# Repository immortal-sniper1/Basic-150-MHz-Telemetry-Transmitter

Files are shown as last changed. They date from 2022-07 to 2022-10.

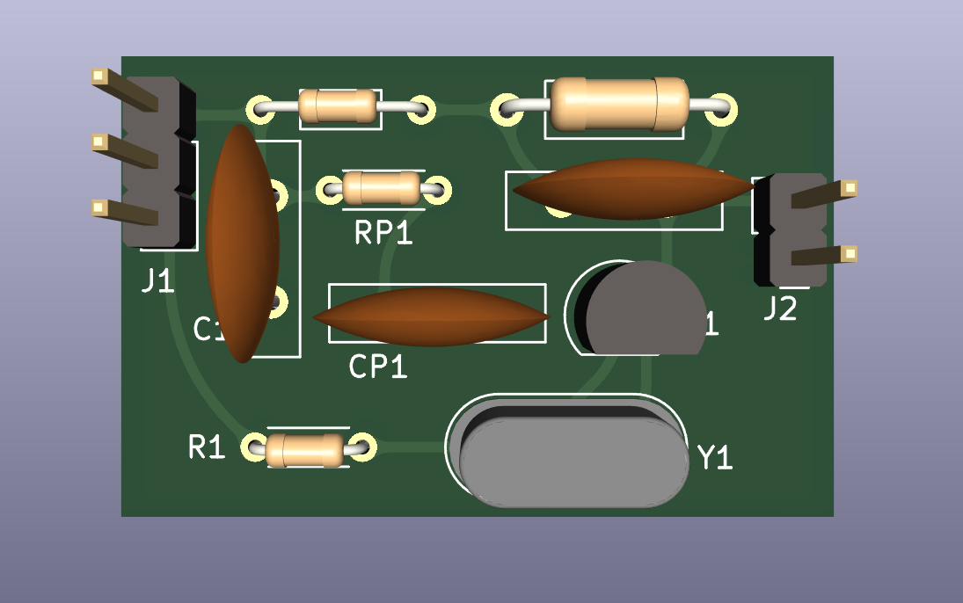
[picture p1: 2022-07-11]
Basic-150-MHz-Telemetry-Transmitter-THT/3d.png

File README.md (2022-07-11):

# Basic-150-MHz-Telemetry-Transmitter      
 Basic 150MHz Telemetry Transmitter based on  https://github.com/fistlabsdev/150-MHz-Telemetry-Transmitter      

Ultra Low Power VHF-Transmitter for Wildlife Radio Tagging      
      
This Transmitter is an adaption of http://http://people.ece.cornell.edu/land/PROJECTS/TRANSMIT/.        
It has some minor changes and uses only discrete components as winding all coils etc. manually needs a lot of experienece, luck and effort to get the circuit running well and robust, which I hardly had to experience... I got two versions running stable, one manufactured in THT and one in SMD.      
      
This circuit allows to build a low-cost, tiny, light weight and very low power VHF-pulse-transmitter from scratch. It's purpose is to be used in scientific tracking applications for wildlife and livestock. This is the easiest but most effective transmitter circuit which is known to me.      
      
This circuit is operating on 150 MHz and as all radio transmitters also emitting electromagnetic waves at harmonic frequencies, so be sure that you now your local rules for the emitted frequency spectrum! This report is only a theoretical abstract so there is no legal warranty.      
      
This circuit is based on developments in the early 70s on radio telemetry for wildlife and still base for many transmitters nowadays. Check also R. Kenwards book "A manual for wildlife radio tagging" if you're interested in further information and advanced knowledge in radio tagging.      
      
The circuit is in principle a very simple single-stage oscillator based on the third harmonic of a 50MHz crystal (you can also use a different frequency crystal). Its emitting short pulses of a continuous wave signal. The pulse width and pulsing frequency is determined by a simple RC-network.
This transmitter can also be used for simple data modulation using ASK (Amplitude Shift Keying) with On-Off-Keying (OOK) by removing the components Rp and Rc and turning on/off the oscillator by applying/removing voltage (with levels Uin/GND) directly to resistor R1 (Node "EN").      

Best results were found with the following values:      
      
C1 = 100 nF      
L1 = 100 nH (In THT wind copper coil: 4x0.4mm, diameter 3mm)     
R1 = 390 kOhm     
C2 = 15 pF      
L2 = 1 µH (In THT wind copper coil: 12x0.4mm, diameter 3mm)     
NPN = MMBT3904 (In THT: 2N3904)     
XTAL = 50 MHz     
3rd harmonic determines transmitter frequency     
        
Rp = 0-1 MOhm     
Cp = 0-5 µF      
Combination of Rp and Cp determine the pulse width and Pulsing frequency.     
     
This circuit can be build on a small pcb (see also eagle schematic and layout in ".../eagle/") or directly solder the THT components to each other as a "flying assembly". As antenna you can use just a piece of copper wire with length lambda/4 which is for 150MHz: 2m/4 = 50 cm      
     
The PCB SMD version got an additional matching capacitor Cm with value 2.2pF which was added in series to the antenna.

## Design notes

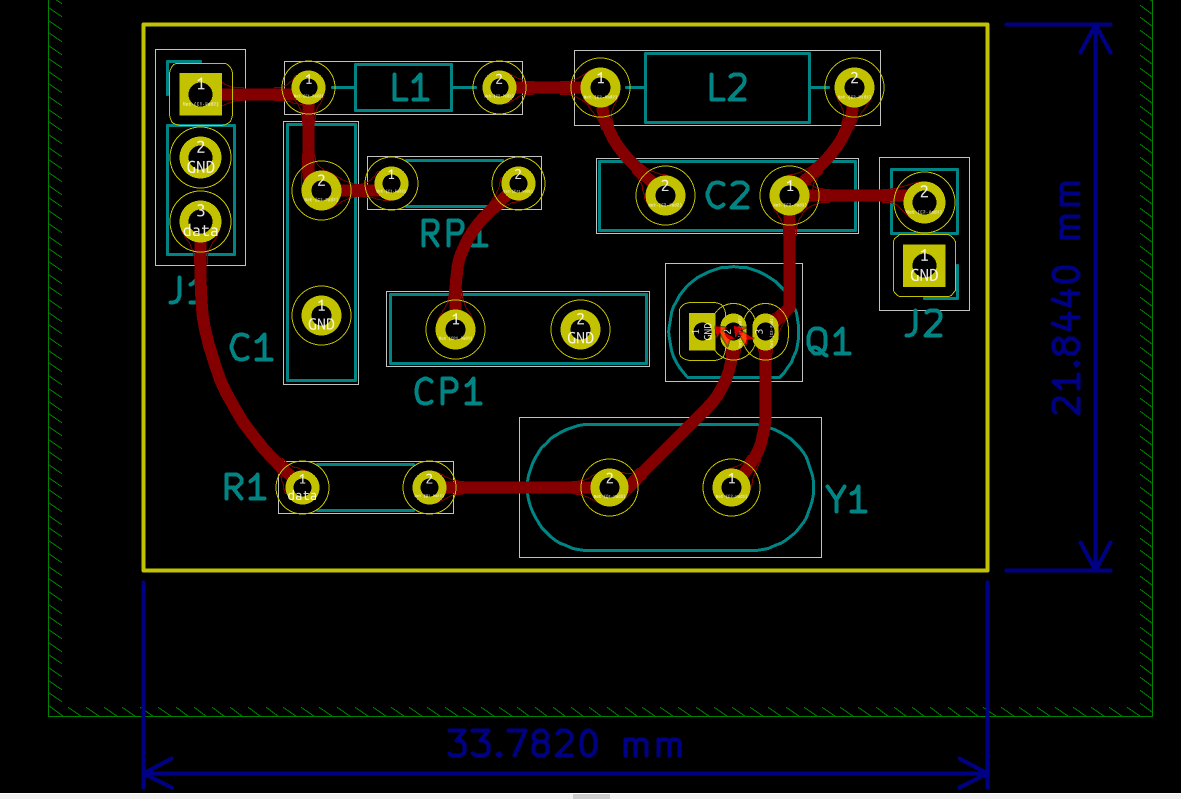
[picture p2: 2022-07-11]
Basic-150-MHz-Telemetry-Transmitter-THT/layout.png

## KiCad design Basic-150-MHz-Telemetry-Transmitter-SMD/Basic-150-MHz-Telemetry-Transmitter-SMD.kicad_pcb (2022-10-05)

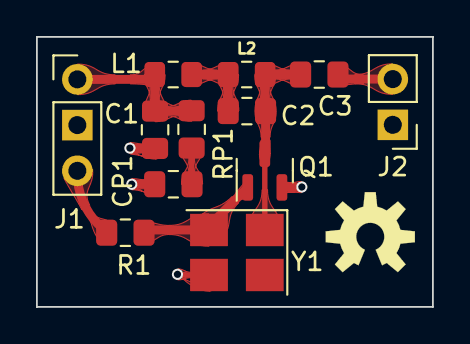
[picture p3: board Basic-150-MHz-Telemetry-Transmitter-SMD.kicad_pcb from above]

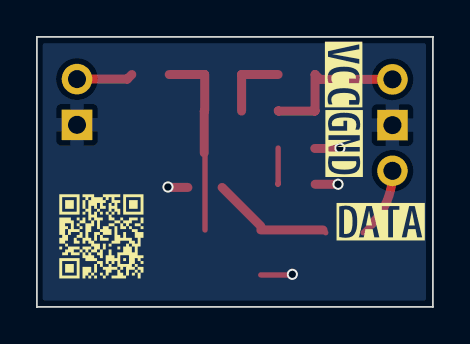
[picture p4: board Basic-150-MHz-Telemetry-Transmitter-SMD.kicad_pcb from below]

Board: 2 copper layers, 22.0 x 15.0 mm, 16 parts (4 on the bottom side), 8 nets.

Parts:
 : LOGO
C1, C2, C3: C_Small; C_0805_2012Metric_Pad1.18x1.45mm_HandSolder
CP1: C_Small; C_0805_2012Metric_Pad1.18x1.45mm_HandSolder
J1: input/output; PinHeader_1x03_P2.54mm_Vertical
J2: Antenna; PinHeader_1x02_P2.54mm_Vertical
L1, L2: INDUCTOR; L_0805_2012Metric_Pad1.15x1.40mm_HandSolder
Q1: MMBT3904; SOT-23
R1: R_Small; C_0805_2012Metric_Pad1.18x1.45mm_HandSolder
RP1: R_Small; C_0805_2012Metric_Pad1.18x1.45mm_HandSolder
Y1: Crystal_GND3; Crystal_SMD_SeikoEpson_FA238V-4Pin_3.2x2.5mm_HandSoldering
kibuzzard-632D4E48: G***; kibuzzard-632D4E48
kibuzzard-632D4E55: G***; kibuzzard-632D4E55
kibuzzard-632D4E64: G***; kibuzzard-632D4E64

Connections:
GND: C1.1, CP1.2, J1.2, J2.1, Q1.2 (E), Y1.3
unnamed: C1.2, J1.1, L1.1, RP1.1
unnamed: C2.1, C3.1, L2.2, Q1.3 (C), Y1.1
unnamed: C2.2, L1.2, L2.1
unnamed: CP1.1, RP1.2
unnamed: C3.2, J2.2
unnamed: Q1.1 (B), R1.2, Y1.2
data: J1.3, R1.1
